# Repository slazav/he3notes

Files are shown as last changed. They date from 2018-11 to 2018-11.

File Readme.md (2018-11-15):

Work reports and notes.
- Folders for each project.
- A tex file with all information and pictures.
- Supplementary files and folders with links from tex.

The idea is to have a complete pdf page with hyperlinks
which can be sent to any external person.

Update script put all files into SITE folder and syncronizes
it with my aalto page (https://users.aalto.fi/~zavyalv1/texts/)

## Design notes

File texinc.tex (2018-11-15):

% standard packages
\usepackage{amssymb}
\usepackage{euscript}
\usepackage{eurosym}
\usepackage{graphicx}
\graphicspath{{img/}}
\usepackage{color}
\usepackage{epsfig}
\usepackage{fullpage}
\usepackage[colorlinks=true]{hyperref}
\usepackage{titling}

% title style
\pretitle{\noindent\LARGE}
\posttitle{\\[1ex]}
\preauthor{\large}
\postauthor{,}
\predate{\large(}
\postdate{)}
\date{last update: \today}

% large page size
\oddsidemargin -1cm
\topmargin -1cm
\textwidth 18cm
\textheight 27cm
\pagestyle{empty}

% PDF figure (floating)
\newcommand{\image}[3]{
\begin{figure}[#1]
\begin{center}
\caption{\small#3}

\label{image:#2}
\end{center}
\end{figure}
}

% simple image
\newcommand\simpleimage[3][\linewidth]{
\smallskip\begin{center}\vbox{\noindent
\\%
\parbox{#1}{\it#3}}\end{center}
\medskip}

%\newcommand\simpleimage[3][\linewidth]{
%\smallskip\vbox{\noindent
%\includegraphics[width=#1]{#2}\\%
%\it#3}
%\medskip}

% companies
\def\SchaefferAG{\href{https://www.schaeffer-ag.de/en/}{Schaeffer-AG}}
\def\MultiCB{\href{https://portal.multi-circuit-boards.eu}{Multi-CB}}
\def\BlueFors{\href{https://www.bluefors.com/}{BlueFors}}

\def\Ohmite{\href{https://www.ohmite.com}{Ohmite}}
\def\Firmetal{\href{http://www.firmetal.com}{Firmetal}}
\def\Bruker{\href{https://www.bruker.com}{Brucker}}

% use this to refer to Farnell and RS numbers:
\def\FarnellN#1{\href{https://fi.farnell.com/#1}{Farnell:#1}}
\def\RSN#1{\href{https://fi.rsdelivers.com/productlist/search?query=#1}{RS:#1}}

% products:
\def\OhmiteOFOD{\href{https://www.ohmite.com/assets/docs/res_od_of_oa.pdf}{Ohmite OF/OD series}}

% Supplementary materials on github <report> <file>
\def\GitFile#1#2{\href{https://github.com/slazav/he3notes/raw/master/#1/#2}{#1/#2}}

% Supplementary materials on my users.aalt.fi page
\def\WWWFile#1{\href{https://users.aalto.fi/~zavyalv1/#1}{#1}}

%progams
\def\MagnettiProg{\href{https://github.com/slazav/magneetti}{\tt magnetti}}

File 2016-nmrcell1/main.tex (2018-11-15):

\documentclass[a4paper]{article}
\input{../texinc.tex}

\title{NMR cell N1 (2016)}
\author{V.Zavjalov}

\twocolumn
\begin{document}
\maketitle

A simple cell for testing NMR in superfluid $^3$He. A Stycast-1266 cylindrical cell,
diameter 7.8~mm, height 10~mm, filling line 1~mm.

All drawings: \WWWFile{notes/2016-nmrcell1/draw.zip}\\
NMR magnet text: \WWWFile{notes/2016-nmrmag.pdf}

\simpleimage{img/cell_plan.png}{RF coil former (left) and the cell (right)}

\simpleimage{img/cell_parts.jpg}{Cell parts}

Copper cell leg was annealed at $900^\circ$C for 2h, brass spacer was
hard-soldered. Cleaning have been done in boiling water (to remove flux),
and then in boiling water with vinegar and baking soda to remove oxide. Note,
that brass became a copper-colored after soldering because Zn goes away.

Small quartz fork (32kHz) have been put into the cell leg about 1 cm from
its bottom. Cell leg have been glued into the cell with Stycast-1266.
Wires from the fork go through the glue.

Fork measurement at room temperature:\\
$P=1$~bar: $1/\tau=17.22$~1/s, $f=32743.76$~Hz\\
$P=0$~bar: $1/\tau=1.364$~1/s, $f=32750.69$~Hz

\simpleimage{img/cell_glue.jpg}{Cell leg (hard-soldered); fork (can is opened); gluing the cell}

Two pairs of RF coils are mounted on a separate plastic holder. Each pair has 34+34 turns
of 70mkm(?) Cu wire. Copper wires are in thermal contact with the mixing chamber.
Measured inductance, capacitance and resistance (with ~30cm wires):\\
coil 1: $L = 55.6\,\mu$H, $C = 14.2$~pF, $R = 14.4\,\Omega$\\
coil 2: $L = 55.4\,\mu$H,  $C = 15.7$~pF,  $R = 14.6\,\Omega$\\
Mutual capacitance about 10~pF.

Calculated magnetic field in the center: 16.6~G/A.
Calculation script (uses \MagnettiProg{} program) and field profile (text table):
\WWWFile{notes/2016-nmrcell1/rfcoil\_calc.zip}

\simpleimage{img/rfcoil_parts.jpg}{Parts of RF coil former}

\simpleimage{img/rfcoil.jpg}{RF coil (final version is on the right)}

\simpleimage{img/cell_finished.jpg}{Cell is mounted on the flange; centering RF coils}

\simpleimage{img/cell_magn.jpg}{The cell and the magnet}

RF coil forms a resonant circuit with a capacitor. A relay box (todo: text)
is used to switch the capacitance from 400 to 2400~pF.

Resonance curves measured at room temperature with a generator and a
lock-in, matlab script for fitting (not good):
\WWWFile{notes/2016-nmrmag/res300K.zip}. At frequency 800~kHz mutual inductance
and parasitic capacitance between coils compensates each other and
coupling goes to zero. This is an ideal situation for such
NMR coil design.

\simpleimage{img/resonance.png}{Resonances at room temperature}

Noise measured at room temperature:\\
\WWWFile{notes/2016-nmrmag/noise300K.zip}

\simpleimage{img/noise300K.png}{Coil noise at room temperature}

{\bf Drilling the cell (2018-01-18).} During glueing the cell filling line
was blocked. The filling line was drilled through the top wall of the cell,
then the hole was glued with a small GRP part.

\simpleimage[3cm]{img/drilling.jpg}{Drilling the cell}

{\bf RF-field calibration in the HPD experiment.} For $U_{\mbox{exc}}=1$~V
voltage on the coil is 0.05~V (HiZ mode of the generator + 20~dB
attenuator). Assuming the inductance~$L=55\,\mu$H and the
frequency~$f=1.120$~MHz one have the current~$I=0.13$~mA and field
$2.14$~mG/V in the center. Dimensionless field is $6.2\times10^{-6}$.

\end{document}

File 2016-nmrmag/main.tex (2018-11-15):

\documentclass[a4paper]{article}
\input{../texinc.tex}

\title{NMR magnet}
\author{V.Zavjalov}

\twocolumn
\begin{document}
\maketitle

NMR magnet for $^3$He experiments in DryDemag cryostat (summer 2016). The bottom flange
is connected to the nuclear demagnetization stage sinter volume. There is
a 6mm CuNi tube for soldering an experimental cell. The coil former is
thermally separated from the nuclear stage by Nb shield (Note: now the
lower part of the coil former is touching the shield. If one makes a
design with a gap there it will be much smaller heat leak through
niobium). The shield fully encapsulates the magnet. In the shield there
is a D6 hole for the cell leg, D3 and D4 screw holes near corners (where
marnetic field is small) and possible gap between Nb tube and top/bottom
plates.

\simpleimage[6cm]{img/solenoid_plan.png}{}
\simpleimage{img/solenoid.jpg}{Solenoid and testing frame}

The coil former and flanges have been made of oxigen-free copper in LTL
workshop and then annealed for 2 hours at 900$^\circ$C in
$2\cdot10^{-3}$~mbar of air (remove hidrogen, oxidize magnetic
impurities, anneal copper for better conductivity). Niobium parts have
been ordered in \Firmetal{} company (534\euro{} for the
$60\times1\times140$~mm tube, 153\euro{} for $65\times140\times1$~mm
plate).

All drawings: coil former, flanges, niobium shield, contact plate,
testing flange: \WWWFile{notes/2016-nmrmag/draw.zip}

\simpleimage{img/parts.jpg}{Magnet parts}

\simpleimage{img/parts_ann.jpg}{Copper parts after annealing}

\subsection*{Magnet calculation}
Coil calculations and optimisation have been done with \MagnettiProg{} program.\\
Optimization details:\\
\WWWFile{notes/2016-nmrmag\_calc.pdf}\\
Script for optimization:\\
\WWWFile{notes/2016-nmrmag/calc\_scr.zip}\\
Calculated field profiles (text table):\\
\WWWFile{notes/2016-nmrmag/calc\_res.zip}

\simpleimage{img/field_prof.png}{Calculated field profiles}

\subsection*{Magnet winding}

Winding was done 20-21.9.2016. Before winding a plastic rod with
longitudinal grooves on the surface have been inserted in the coil former
to prevent its deformation. After winding it was removed by drilling.

{\bf Wire.} Vacryflux 5001. 54 NbTi filaments in Cu matrix; diameter:
$70\mu$m without isolation, $83-85\mu$m with isolation; Cu/NbTi ratio:
1.35/1; critical current: 2~A at 3~T, 1~A at 8~T; resistance at room
temperature $8.0\Omega/$m; bought from \Bruker. Stycast-1266 was used to
fill the coil.

\simpleimage{img/winding.jpg}{Winding process}

{\bf Main coil:} length 104~mm, inner diameter 42~mm. Winding:
5 layers: 1208+1197+1200+1203+1193 turns. Accurate everywhere except
~4mm edges (hard to move from one layer to another with such a thin
wire). Then flatten edges with 12mm Kapton. Then 3 layers 11.2mm (compensation + 6thlayer):
140+97+120 turns. Then middle part of the 6th layer: 939 turns. Then
3 layers 11.2mm (compensation + 6thlayer): 133+103+133 turns.
Number of turns in the compensation coils is the same on both sides,
but it is a bit smaller then it should be.

{\bf Quadratic coil.} $L=34.8$, 2 layers, 408+408 turns.
After the coil had been made, the solenid was fully covered with Kopton
tape, and then by two layers of white paper to make a flat surface for
next coils.

{\bf Gradient coil.} Start at 2mm from solenoid edges, L=41.8mm R=~21.5
1 layer, 514+482 turns (not so accurate andassymetric).
Then the central part was covered with red "yellow" tape to make it flat
for the next coil.

{\bf Forth-power coil.} 1 layer, 79+79 turns, 6.8mm + 14mm gap + 6.0mm
(very assymetric for some reason).

\simpleimage{img/main_coil.jpg}{Main coil}

\simpleimage{img/grad_coil.jpg}{Gradient coil}

\simpleimage{img/coil.png}{Coil layout}

{\bf Connector:} plastic body + brass screws and nuts +
two-sided 0.4mm PCB (one side for contacts, another one for heat sink).
Wires are soldered to the connector at length 20-30cm (isolation was
removed in boiling NaOH).

\simpleimage{img/conn.jpg}{Connector}

\simpleimage{img/final.jpg}{Flanges}

\subsection*{Solenoid parameters}

Field profile, calculated and measured by shift of $^3$He NMR line:

\medskip
\begin{tabular}{llll}
Coil  &  Field [G/A] vs r,z [cm] & measured\\\hline
Main   &  $397.996$                       & $407.72$\\
Grad   &  $31.4270\ z$                    & $1.43 + ? z$\\
Quad   &  $105.958 - 15.240 f_2$$^{(1)}$  & $108.27 - ? f_2$\\
Helm   &  $16.6512 - 1.0351 f_4$$^{(2)}$  & $18.09 - ? f_4$\\
\end{tabular}

\noindent
(1) $f_2 = z^2-r^2/2$\\
(2) $f_4 = z^4 - 3 z^2 r^2 + 3/8 r^4$
\medskip

For comparison, Rota quadratic coil in magnon condensate experiments was $2.231 - 3.304 f_2$

Errors, calculated in cylindrical volumes with length = diameter 10 and 20 mm,
and measured by normal $^3$He NMR line width.

\medskip
\begin{tabular}{llll}
Coil   & Err 20x20 & Err 10x10 & Err (measured) \\\hline
Main   & $1.4\cdot10^{-5}$ & $2.2\cdot10^{-6}$ & $\approx1\cdot10^{-4}$\\
Grad   & $1.5\cdot10^{-2}$ & $3.5\cdot10^{-3}$ & \\
Quad   & $4.9\cdot10^{-3}$ & $3.0\cdot10^{-4}$ & \\
Helm   & $1.8\cdot10^{-1}$ & $2.2\cdot10^{-1}$ & \\
\end{tabular}
\medskip

Coil resistances:

\medskip
\begin{tabular}{ll}\hline
Main: & 7980~$\Omega$\\
Grad: & 1068~$\Omega$\\
Quad: & 861~$\Omega$\\
Helm: & 174~$\Omega$\\
\end{tabular}
\medskip

On the connector all coils are shortened by 100~$\Omega$ resistors to
provide LR filtering.

\subsection*{Problems and ideas}

1. Cut lower flange of the coil former to avoid contact with niobium shield and
decrease heat conductivity. I am not sure that this can be done accurately.
Also I'm not sure that this heat leak source is important.

2. Problem with the gradient coil: measurement gives approximately 1/2 of the
calculated value (15~G/cm/A). A stupid mistake somewhere...

3. One lead of the main coil is connected to the ground. Probably, can
not be fixed.

\end{document}

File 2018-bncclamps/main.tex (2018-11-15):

\documentclass[a4paper]{article}
\input{../texinc.tex}

\title{BNC clamps}
\author{V.Zavjalov}

\twocolumn
\begin{document}
\maketitle

In CW NMR experiments with compensated signal unstable contact in BNC
connectors is a problem. Unfortunately, most of usual devices use such
connectors for signal lines. There are a few ways how one can deal with
this problem. In Dmitriev's group in Moscow all important connectors have
been replaced to TNC (a threaded version of the BNC). This needs
disassembling of devices and not always possible. In ROTA group in
Helsinki clamps have been used to attach BNC-to-SMA converters to all
connectors.

\simpleimage{img/clamp_rota.jpg}{ROTA clamp}

I am using similar clamps as in ROTA but simpler and cheaper. Clamps have
been ordered in \SchaefferAG{} company. Price was 332\euro{} for 20
aluminum clamps (two parts each). Aluminum is a bit too soft, one should
try thicker design or different metal. But clamps work pretty well.

\noindent Clamp drawing, FPD files for production:\\
\WWWFile{notes/2018-bncclamps/fpd\_v1.zip}

\begin{center}
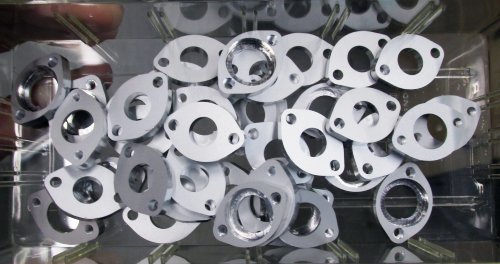
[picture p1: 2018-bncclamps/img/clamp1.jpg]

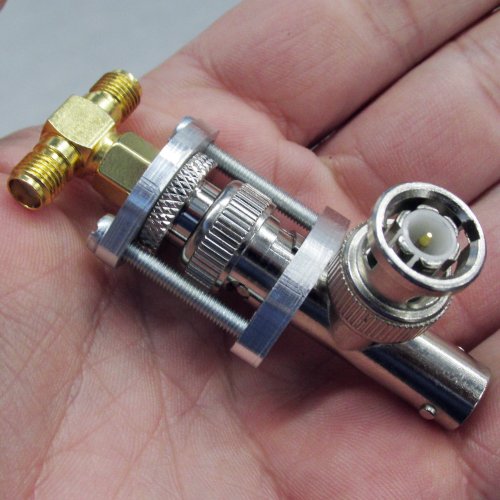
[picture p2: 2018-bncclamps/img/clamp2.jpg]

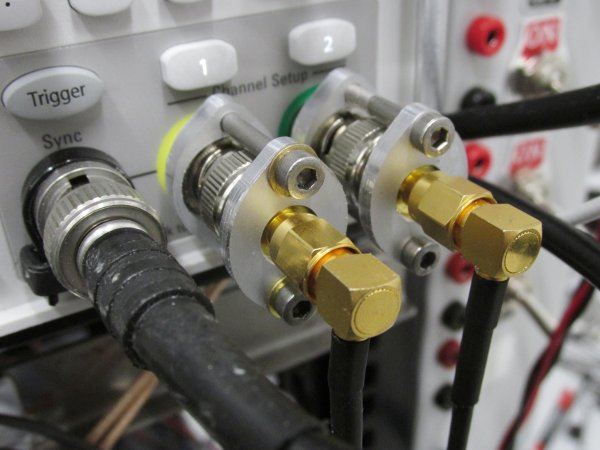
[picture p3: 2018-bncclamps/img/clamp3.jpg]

\end{center}

\end{document}

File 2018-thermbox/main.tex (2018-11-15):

\documentclass[a4paper]{article}
\input{../texinc.tex}

\title{Carbon thermometers for dilution fridges}
\author{V.Zavjalov}

\twocolumn
\begin{document}
\maketitle

The goal is to make standard thermometers for use in dilution fridges. I
use carbon \Ohmite{} resistors (\OhmiteOFOD{}, \FarnellN{2427380},
\FarnellN{2427405}, \RSN{892-5449} etc.), which are claimed to be
good thermometers at millikelvin temperatures~\cite{therm_paper}. The
series OD and OF have different sizes (diameter $2.5$~mm and~$3.8$~mm and
length~$7$~mm and~$10$~mm respectively). I grind resistors down to
approximately $0.7$~mm thickness and glue it in a slit in a copper box
using Stycast 2850. This provides a good thermal contact with the box,
mechanical stability, and protection against moisture.

\begin{center}
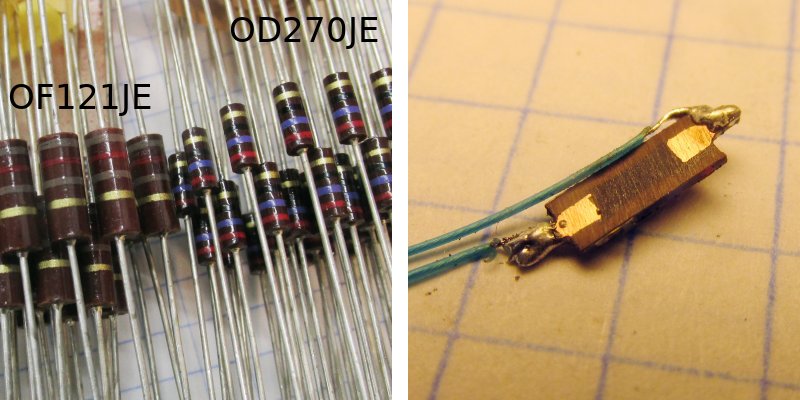
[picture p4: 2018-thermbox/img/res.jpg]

\end{center}

Copper boxes are ordered in \SchaefferAG.  The
box has $30\times30\times5$~mm size. It contains a~$20\times18\times3$~mm
compartment for RC lowpass filters, a $1\times16\times4$~mm slit for the
resistor and a~$16\times7\times3$~mm additional compartment which can be
used for sample chips. Holes are compatable with standard~$20\times20$ M4
hole grid on \BlueFors{} refrigerator plates. Drawings in FPD format are
available~\cite{box_drawings}, price was 315\euro{} for 10 boxes and 10
lids.

\begin{center}
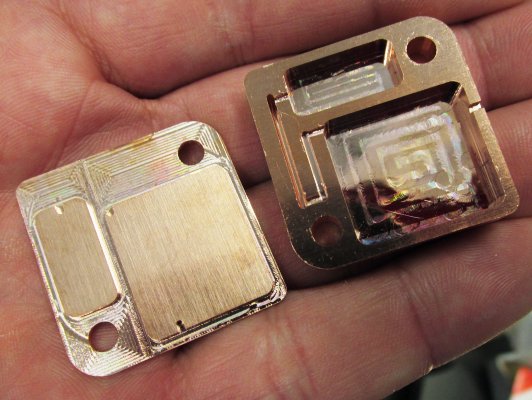
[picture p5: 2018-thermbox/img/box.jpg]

\end{center}

PCBs for filters are ordered in \MultiCB. Price
is 75\euro{} for 10 boards with two different filters and two small
sample plates each. Kicad project~\cite{filterpcb-kicad} and Gerber
files~\cite{filterpcb-gerber} are available.

To connect thermometers to BlueFors 4-pin sockets we use inserts
of LEMO {\tt FFA.0S.304.CLAC44} connectors (\FarnellN{2442870}).

\begin{center}
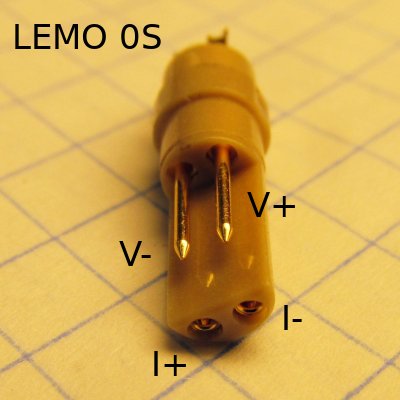
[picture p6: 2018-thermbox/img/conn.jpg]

\end{center}

\subsection*{List of devices}

\noindent
\begin{tabular}{|ll lll l|}\hline
N& Resistor& $R_0$ & $R_1$ & $R_2$ & \\
\hline
2018-11-02 N1&OD270JE& 27  & 56  & 56.0&\\
2018-11-02 N2&OD270JE& 27  & 59  & 64.4&\\
2018-11-02 N3&OF121JE& 120 & 231 & 277&\\
\hline
\end{tabular}
\medskip

Here $R_0$, $R_1$, and $R_2$ are nominal resistance, resistance after
grinding, and resistance after soldering and glueing. Change during
glueing probably means that contacts with carbon in the resistor
after grinding are not stable.

{\bf Work in progress...}

\begin{thebibliography}{}
\bibitem{therm_paper}
N. Samkharadze, A. Kumar, G. A. Cs{\'a}thy,
A New Type of Carbon Resistance Thermometer with.Excellent Thermal Contact at Millikelvin Temperatures,
{\it JLTP}, {\bf 160}, 246--253 (2010),\\
\url{https://doi.org/10.1007/s10909-010-0192-5}

\bibitem{box_drawings}
Box drawing in FrontPanel Disigner format, for production,\\
\WWWFile{notes/2018-thermbox/box\_v1.zip}

\bibitem{filterpcb-kicad}
Filter PCB, KiCAD project,\\
\WWWFile{notes/2018-thermbox/pcb\_kicad.zip}

\bibitem{filterpcb-gerber}
Filter PCB, Gerber files for production,\\
\WWWFile{notes/2018-thermbox/pcb\_v1.zip}

\end{thebibliography}
\end{document}

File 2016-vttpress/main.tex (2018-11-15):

\documentclass[a4paper]{article}

\input{../texinc.tex}

\title{Calibration of VTT pressure sensor}
\author{V.Zavjalov}

\twocolumn
\begin{document}
\maketitle

{\bf Experimantal setup.} For measurements we used Andeen-Hagerling AH
2500A capacitance bridge working at 1~kHz. The voltage~$U$ applied by the
bridge to the pressure sensor can be chosen in the range from 0.5~mV to
15~V RMS. At~$U>1$~V the noise of the measurement was about
$1\cdot10^{-3}$~pF, this corresponds to the pressure variations of about
$0.3$~mbar. Pressure was measured by Wallace \& Tiernan absolute pressure
gauge with working range $0\ldots1$~bar and resolution $\sim 0.3$~mbar.
%(For low pressure measurements we also use Agilent FRG-730 Pirani gauge.)
Temperature was measured by PT1000 platinum thermometer.

%%%%%%%%%%%%%%%%%%%%%%%%%%%%%%%%%%%%%%%%%%%%%%%%%%%%%%%%%%
\image{h}{pcal}{Fig.~1. (A) Capacitance of the pressure sensor as a
function of pressure. Measurements for three exctation voltages (red 15
V, green 7.5 V, blue 1.5 V) and two temperatures (circles 295~K, squares
77.2~K) are shown. Lines are fits to the model~(\ref{eq:mod}), made
separately for each temperature. Data for other voltage values (3~V,
0.75~V, 0.35~V, 0.25~V, 0.1~V) was used for fitting, but not shown on the
picture.
(B) Difference between measured data and
model~(\ref{eq:mod}). Same data as on (A) are presented. }
%%%%%%%%%%%%%%%%%%%%%%%%%%%%%%%%%%%%%%%%%%%%%%%%%%%%%%%%%%

{\bf Pressure dependence.} We found that at constant temperature the
capacitance~$C$ of the pressure sensor as a function of pressure~$P$ and
applied voltage~$U$ can be fit by a model with four parameters, $C_0$,
$C_1$, $P_0$, $U_0$:
\begin{equation}\label{eq:mod}
C = C_0 + C_1\ \frac{1}{d},
\end{equation}
where $d$ is determined by a non-linear equation:
\begin{equation}
d = 1 - \frac{P}{P_0} - \left(\frac{1}{d}\ \frac{U}{U_0}\right)^2.
\end{equation}
In this model the sensor is treated as a sum of a constant capacitor
$C_0$ and a flat capacitor $C_1$ with dimensionless distance~$d$ affected
linearly by applied force. One component of the force is proportional to
the pressure and another one is electrostatic force proportional to $U^2/d^2$. In
this model the capacitor is collapsed at $P=P_0$ or
$U=2/(3\sqrt{3})\,U_0\approx 0.385\,U_0$. We checked that above~$\approx 1.6$~bar
loss in the capacitor grows quickly and it becomes imposiible to measure
the capacitance.

Fig. 1 shows measured capacitance as a function of~$P$ and~$U$ at room
temperature (295 K) and temperature of liquid nitrogen (77.2~K). One can
see that model works well everywhere except the region of high pressures
and high excitation voltages (this corresponds to the smallest values of
distance~$d$). At small exitation voltages ($<3V$) the model gives us the
accuracy $\sim 10^{-3}$~pF comparable to the noise in the capacitance measurement.

Measured parameters for room temperature (295K), temperature of liquid
nitrogen (77.2 K) and temperature of liquid helium (4.2K) are in the
table:

\begin{tabular}{lll}
$T$, K & $C_0$, pF          & $C_1$, pF \\\hline
295.04 & $24.0821\pm0.0084$ & $9.0052\pm0.0082$\\
77.2   & $23.4230\pm0.0065$ & $8.8738\pm0.0064$\\
4.2    & $23.3702\pm0.0098$ & $8.8544\pm0.0096$\\
\hline
\end{tabular}

\begin{tabular}{llll}
$T$, K & $P_0$, bar & $U_0$, V RMS\\\hline
295.0 & $2.9864\pm0.0019$ & $178.854\pm0.691$\\
77.2  & $3.0082\pm0.0015$ & $179.846\pm0.530$\\
4.2   & $3.0043\pm0.0023$ & $171.643\pm0.713$\\
\hline
\end{tabular}
\medskip

%{\bf Temperature dependence.}
%Measurements similar to Fig.~1 are done at several temperatures giving us
%parameters $C_0$, $C_1$, $\alpha$ and~$\beta$. We also performed
%measurements of the capacitance during slow heating at 0 and 1 bar with
%various voltages~$U$.
%
%TODO

{\bf Helium diffusion.} In helium atmosphere pressure readings of the
sensor start to shift because of diffusion of helium inside the sensor
inner volume. In air or vacuum the diffusion goes in the opposite
direction, restoring the original readings. This effect exist only at
high temperatures. At room temperature we observed filling of the inner
volume with time constant $\sim2.5$~h. At temperature of liquid nitrogen
(77.2~K) we have not observed any visible change during 15~h
(See Fig~2.).

%%%%%%%%%%%%%%%%%%%%%%%%%%%%%%%%%%%%%%%%%%%%%%%%%%%%%%%%%%
\image{h}{hdiff}{Fig.~1. Helium diffusion. At room temperature
(295 K) helium diffuse into sensor's inner volume, filling it with time
constant $\sim 2.5$~h. At temperature of liquid nitrogen no diffusion have
been observed.}
%%%%%%%%%%%%%%%%%%%%%%%%%%%%%%%%%%%%%%%%%%%%%%%%%%%%%%%%%%

\end{document}

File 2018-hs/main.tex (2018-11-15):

\documentclass[a4paper]{article}
\input{../texinc.tex}

\title{Rebuilding heat switch and nuclear stage plate for DryDemag}
\author{V.Zavjalov}

%\twocolumn
\begin{document}
\maketitle

The goal is to make a detachable frame with the nuclear demagnetization
stage (NS) and the heat switch (HS). We try to get more rigid
construction, more space for experiment cells, better heat switch.

\subsection*{Old construction}

In the previous setup NS is mounted on a brass plate (which can be bad
because of large heat capacitance and small heat conductivity of brass).
The plate is hanging on four ceramic legs under the mixing chamber of
DryDemag refregirator~\cite{drydemag}.

\image{h}{old_setup}{}
%\begin{center}
%\includegraphics[width=\linewidth]
%\end{center}

Drawings:
\begin{itemize}
\item Assembly drawing (as on the figure above):\\
\GitFile{20181105-hs}{old\_nsframe\_assembly.pdf}

\item Old brass NS flange drawing:\\
\GitFile{20181105-hs}{old\_flange\_brass.pdf}

\item Old stage flange drawing:\\
\GitFile{20181105-hs}{old\_flange\_brass.pdf}

\end{itemize}

\subsection*{Old HS performance measurements}

\subsection*{HS papers}

\subsection*{Parts}

\begin{thebibliography}{}

\bibitem{drydemag}
I. Todoshchenko, J.-P. Kaikkonen, R. Blaauwgeers, P. J. Hakonen, A. Savin,
Dry demagnetization cryostat for sub-millikelvin helium experiments: Refrigeration and thermometry,
{\it Rev.Sci.Instr}, {\bf 85}, 085106 (2014),\\
\url{https://doi.org/10.1063/1.4891619}

\bibitem{nsframe_fpd}
NS frame (top, middle, and NS plates), FPD files used for ordering parts in Schaefer-AG
\url{nsframe_fpd.zip}

\end{thebibliography}
\end{document}

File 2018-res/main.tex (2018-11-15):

\documentclass[a4paper]{article}
\input{../texinc.tex}

\title{A resonator driven by external force}
\author{V.Zavjalov}

\begin{document}
\maketitle

\begin{tabular}{ll}
\hline\\[-2mm]

Equation: &
$\displaystyle
\ddot x = -\omega^2_0 x + \dot x /\tau + F\exp(i\omega t)$
\\[5mm]

Fourier component~$\omega$: &
$\displaystyle
-\omega^2 x = -\omega^2_0 x + i \omega x /\tau + F$
\\[5mm]

Complex amplitude: &
$\displaystyle
x(\omega) = \frac{F}{\omega_0^2 - \omega^2 - i \omega /\tau}$

\\[5mm]\hline\\[-2mm]

Dispersion: &
$\displaystyle
\Re(x) = F\ \frac{\omega_0^2 - \omega^2}
                {(\omega_0^2 - \omega^2)^2 + (\omega /\tau)^2}$
\\[5mm]
Dispersion max/min: &
$\displaystyle
\omega_m^2 = \omega_0^2 \left(1 \pm \frac1{\omega_0\tau}\right),
\qquad \Re(x) = \mp \frac{F\tau} {2\omega_0 \pm 1/\tau}$
\\[5mm]
Dispersion zero: &
$\displaystyle
\omega_z = \omega_0$

\\[5mm]\hline\\[-2mm]

Absorption: &
$\displaystyle
\Im(x) = F\ \frac{\omega /\tau}
                {(\omega_0^2 - \omega^2)^2 + (\omega /\tau)^2}$
\\[5mm]
Absorption maximum: &
$\displaystyle
\omega_m^2 = \frac13 (\omega_0^2-1/2\tau^2) + \frac13 \sqrt{(\omega_0^2-1/2\tau^2)^2 + 3\omega_0^4}$
\\[5mm]

at $(\omega_0\tau)^2 \gg 1$: &
$\displaystyle
\omega_m^2 \approx \omega_0^2 \left(1 - \frac1{(2\omega_0\tau)^2}\right),
\qquad
\Im(x) \approx \frac{F \tau}{\omega_0}
\left(1 + \frac1{(4\omega_0\tau)^2}\right)
$
\\[5mm]

$1/2$-height points:&
$\displaystyle
\omega_h \approx \omega_m \pm 1/2\tau
$

\\[5mm]

width at $1/\sqrt2$ height:&
$\displaystyle
d\omega \approx \frac1{\tau}
$

\\[5mm]\hline\\[-2mm]

Absolute value: &
$\displaystyle
|x| = \frac{F} {\sqrt{(\omega_0^2 - \omega^2)^2 + (\omega /\tau)^2}}
$\\[5mm]

Absolute value maximum: &
$\displaystyle
\omega_m^2 = \omega_0^2 \left(1 - \frac1{2(\omega_0\tau)^2}\right),
\qquad
|x| = \frac{F\tau}{\omega_0} \left(1 - \frac1{(2\tau\omega_0)^2}\right)^{-1/2}
$
\\[5mm]

$1/\sqrt2$-height points:&
$\displaystyle
\omega_h^2 = \omega_0^2 - 1/2\tau^2 \pm \sqrt{ \omega_0^2/\tau^2 - 1/4\tau^4}
$
\\[5mm]

width at $1/\sqrt2$ height:&
$\displaystyle
d\omega \approx \frac1{\tau} \left(1 - \frac1{8(\tau\omega_0)^2}\right)
$
\\[5mm]\hline\\[-2mm]

\end{tabular}

\section*{Free decay}
\begin{tabular}{ll}
\hline\\[-2mm]

Equation: &
$\displaystyle
\ddot x = -\omega^2_0 x + \dot x /\tau$
\\[5mm]

Solution: &
$\displaystyle
x = C \exp(wt),
\qquad
w = \pm i \sqrt{ \omega^2_0 - 1/4\tau^2} + 1/2\tau
$
\\[5mm]

\end{tabular}

\image{h}{res}{}

\end{document}

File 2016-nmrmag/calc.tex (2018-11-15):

\documentclass[a4paper]{article}

\input{../texinc.tex}

\title{NMR magnet optimization}
\author{V.Zavjalov}

\begin{document}

\maketitle

The field is calculated in radial coordinates,~$r$ and~$z$.
We need to optimize at least three coil systems in the volume $V_0$: $r<r_0, |z|<z_0$:
\begin{itemize}
\item Homogeneous field produced by main solenoid and compensation coils
\item Gradient field
\item Minimum (quadratic) field
\end{itemize}
For this we calculate mean square difference from the best
constant, linear, or quadratic approximation.

$$ R = \sqrt{\frac{1}{V_0}\int_V(H(r,z) - H_0 - A f(z,r))^2\,dV}
$$

Function $f(z,r)$ can be chosen according with the fitting model:
$f(z,r)=0$ for constant field, $f(z,r)=z$ for gradient field, 
$f(z,r)=z^2-r^2/2$ for quadratic field or even $f(z,r) = z^4 - 3z^2r^2 + 3/8r^2$
for forth-order field.

The $-1/2$ ratio of~$r$ and~$z$ quadratic terms comes from Maxwell equations
for a cylindrically symmetric system (see below).

This can be rewritten as
$$ R^2
 = I_2 - 2H_0 I_1 + H_0^2 + A( A I_{f2} - 2I_{fH} + 2H_0 I_{f1})
$$

where we introduced integrals
$$
I_1 = \frac{1}{V_0}\int_V H(z,r)\, dV,\qquad
I_2 = \frac{1}{V_0}\int_V H(z,r)^2\, dV,\qquad
$$
$$
I_{fH} = \frac{1}{V_0}\int_V f(z,r) H(z,r)\, dV,\qquad
I_{f1} = \frac{1}{V_0}\int_V f(z,r)  \, dV,\qquad
I_{f2} = \frac{1}{V_0}\int_V f(z,r)^2\, dV,\qquad
$$

Parameters $H_0$ and $A$ correspond the minimum of~$R$:
$$
\frac{\partial R}{\partial H_0} = 0,\quad
\frac{\partial R}{\partial A} = 0
$$

$$
H_0 = I_1 - A I_{f1},\qquad
$$
$$
A = (I_{fH} - I_{f1} I_1)/(I_{f2} - I_{f1}^2),\qquad
$$

For coil optimizations we use dimensionless current-independent
parameters:
$R/|H_0|$ for constant field, $R/(z_0|A|)$ for gradient field, and
$R/(z_0^2|A|)$ for quadratic fields.

Optimization is done in $z0=r0=10$ cylindrical volume.

{\bf Main coil geometry.} We use main coil with length 104~mm, inner radius
21~mm, and 6 layers of wire in the cylindrical shield with length 140~mm
and radius 29~mm. Wire diameter is 0.084mm (in insulation).

{\bf Compensation coils.} Minimum value in the optimization is not so
important as the minimum width ($0.2$~mm error will break all the
improvements). It's better to start compensation coils from edge of the
main solenoid and make them thin (I use 2 layers) and long -- then the
minimum is wider. Shorter coils have better field homogeneity, but it is
harder to make accurate size. Second layer with different length does not
help much. Compensation coils inside the solenoid is slightly better, but
i decided to put them outside to adjust size after making and
recalculating the main solenoid. Also it is easier to wind the main solenoid
on a flat surface. The quadratic coil can improve the field
homogeneity even more.

{\bf Gradient coils} are better if they are wider. It is good to start
them from the edge of the solenoid. Starting from the end of compensation
coils is also fine (\%10 worse). Second layer with different length can
improve gradient accuracy $\approx 2$ times,

{\bf Quadratic coil} just a coil in the center with a certain width.

{\bf Optimization results:}\\
\medskip
\begin{tabular}{lllllll}
Coils & Edge &Length       & Layers & Err 20x20$^{(1)}$  & Err 10x10$^{(2)}$        & Field [G/A] vs r,z [cm] \\\hline
Main  & 52   & 104         & 6      & $6.6\cdot10^{-4}$ & $1.7\cdot10^{-4}$ & $397.086$\\
Comp  & 52   & 11.2        & 2      & $1.4\cdot10^{-5}$ & $2.2\cdot10^{-6}$ & $397.996$\\
Grad  & 50   & 41.8        & 1      & $1.5\cdot10^{-2}$ & $3.5\cdot10^{-3}$ & $31.4270\ z$\\
Quad  & -    & 34.8        & 2      & $4.9\cdot10^{-3}$ & $3.0\cdot10^{-4}$ & $105.958 - 15.240 (z^2-r^2/2)$\\
4-th  & 13.4 & 6.4         & 2      & $1.8\cdot10^{-1}$ & $2.2\cdot10^{-1}$ & $16.6512 - 1.0351 f_4$$^{(3)}$\\
\end{tabular}
\medskip

\noindent
(1) in the volume with length = diameter = 20 mm.\\
(2) in the volume with length = diameter = 10 mm.\\
(3) $f_4 = z^4 - 3 z^2 r^2 + 3/8 r^4$

\section*{Field distribution in a cylindrical simmetry (why $z^2+r^2/2$)}

Maxwell equations:
$$
\mbox{div} B = 0,\qquad
\mbox{rot} B = 0
$$

In symmetrical case ($\partial B/\partial\phi = 0, B_\phi=0$):
$$
\frac{\partial B_r}{\partial z} = \frac{\partial B_z}{\partial r}, \qquad
\frac{1}{r} \frac{\partial r B_r}{\partial r} + \frac{\partial B_z}{\partial z}=0.
$$

Multiply the first equation by $r$, differentiate by $r$, and then multiply by $1/r$.
Differentiane the second equation by $z$. Then one can exclude $B_r$:
$$
\frac{1}{r} \frac{\partial B_z}{\partial r}
 + \frac{\partial^2 B_z}{\partial r^2}
 + \frac{\partial^2 B_z}{\partial z^2}=0.
$$

For quadratic distribution $B_z = az^2 + br^2$ one have $a=-2b$.

For 4-power distribution $B_z \propto z^4 - 3 z^2 r^2 + 3/8 r^4$.

\section*{Critical current}

For calculated solenoid (main + compensation coils), maximum absolute
field on the coil is 0.110~T/A, on the shield is 0.843~T/A.
According with Bruker wire specification critical field is $(13-5I)$~T.
Critical field for Nb shield as about 0.15~T.

Thus the current limit introduced by shield is 1.35~A,
current limit by wire is 2.57~A. This corresponds to the
field in the middle 0.09~T and 1.71~T (???).

\end{document}

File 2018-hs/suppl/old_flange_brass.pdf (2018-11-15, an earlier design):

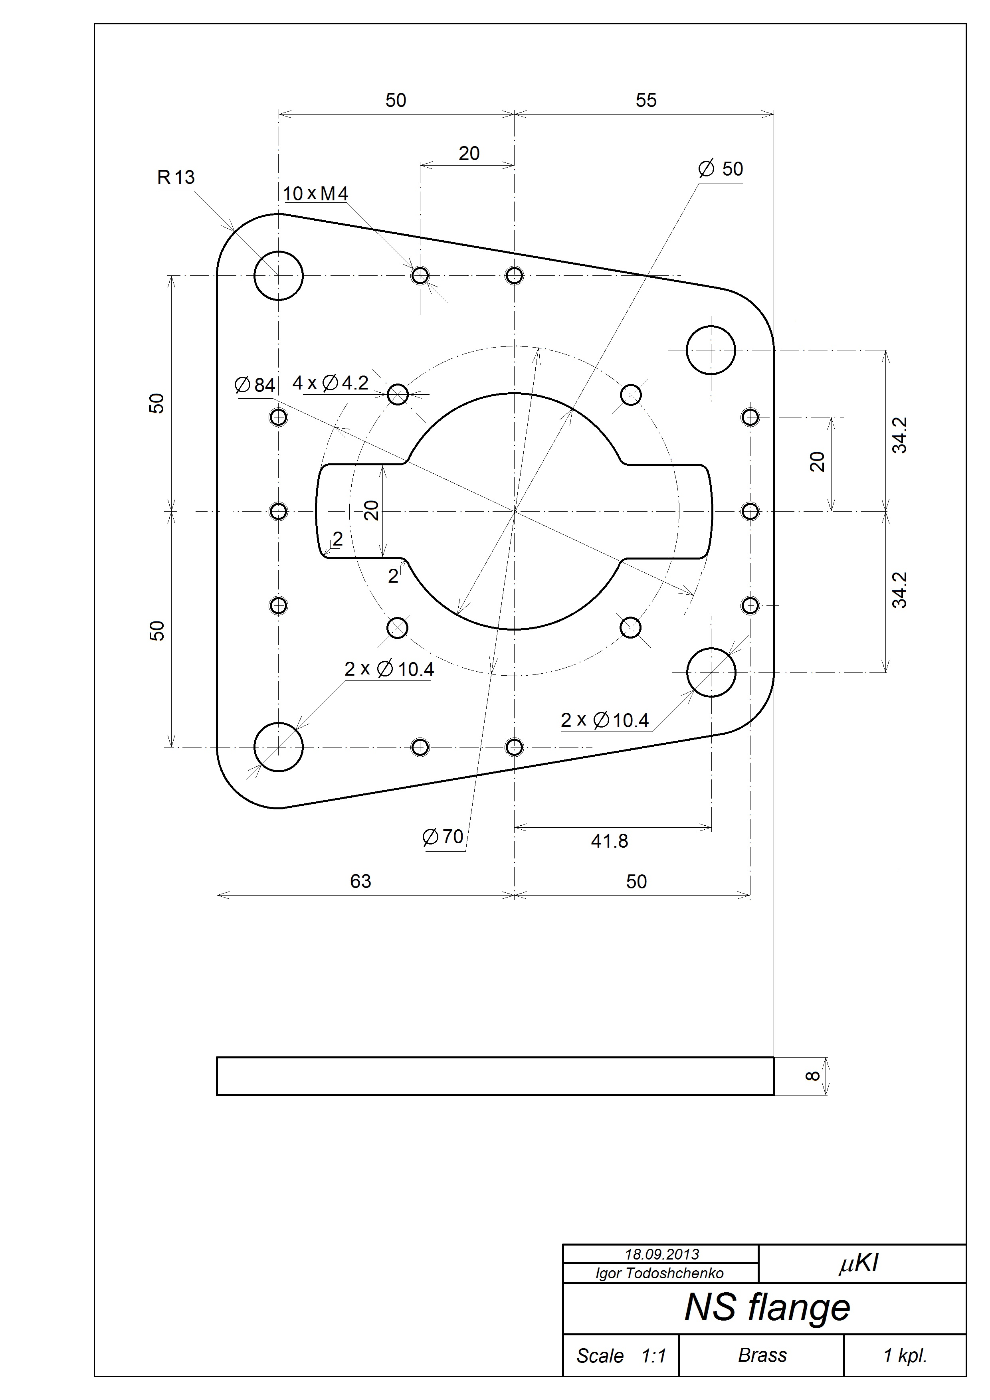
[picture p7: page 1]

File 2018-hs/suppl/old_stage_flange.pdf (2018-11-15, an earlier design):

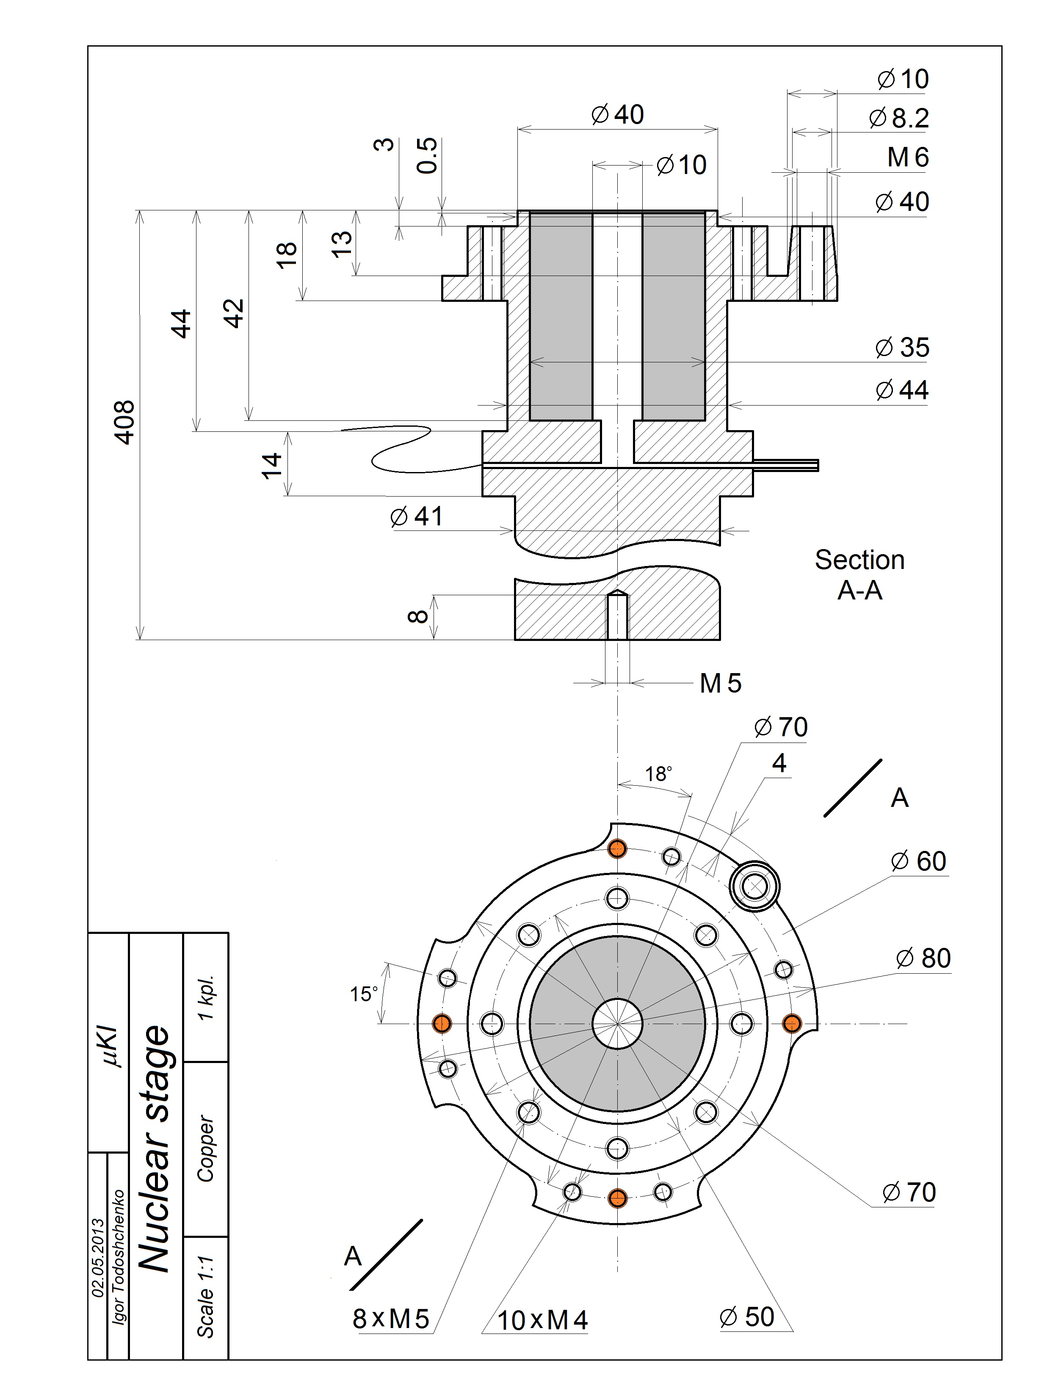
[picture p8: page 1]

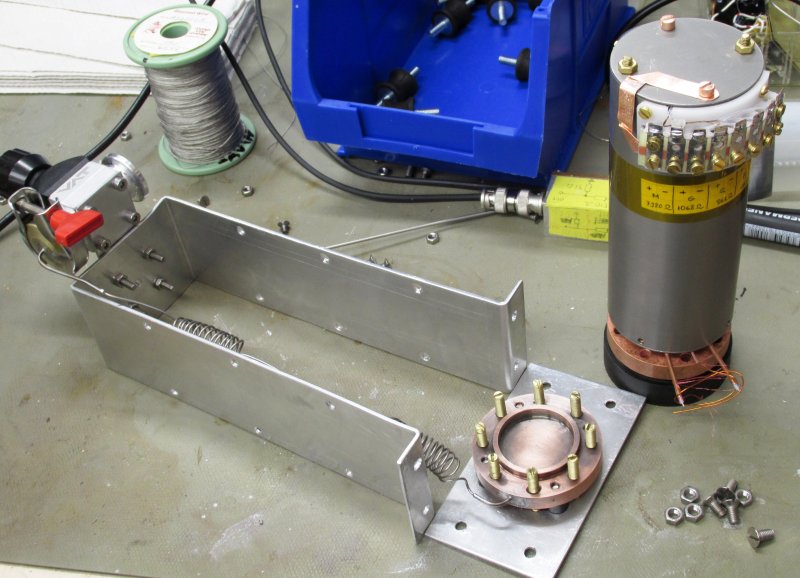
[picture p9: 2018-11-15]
2016-nmrmag/img/solenoid.jpg

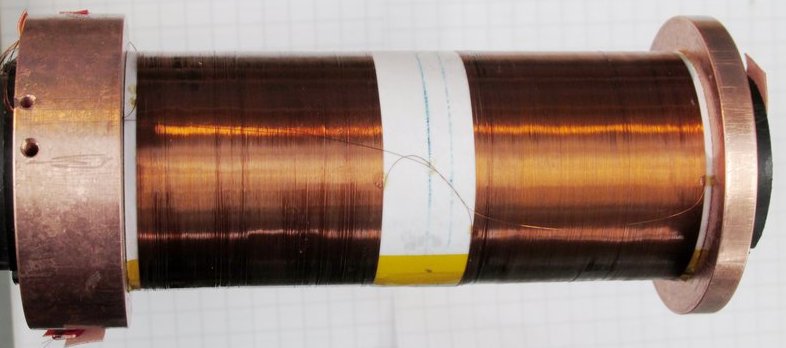
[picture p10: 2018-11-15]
2016-nmrmag/img/grad_coil.jpg

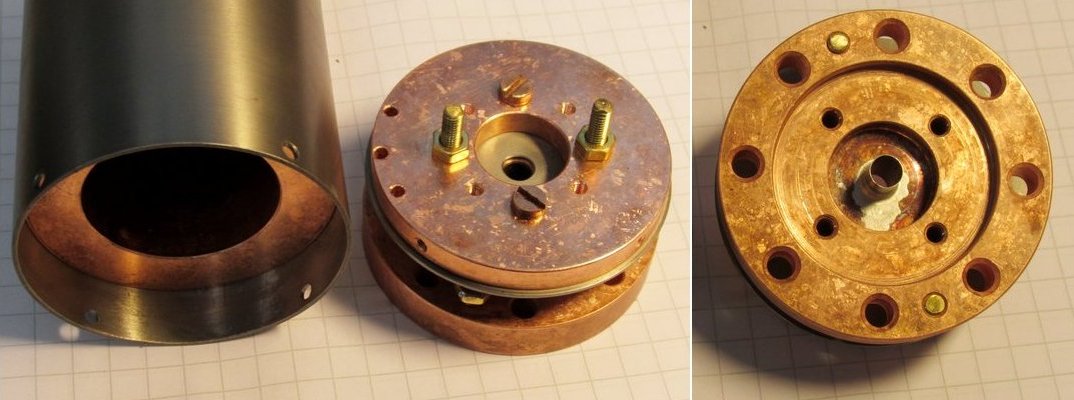
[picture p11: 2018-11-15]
2016-nmrmag/img/final.jpg

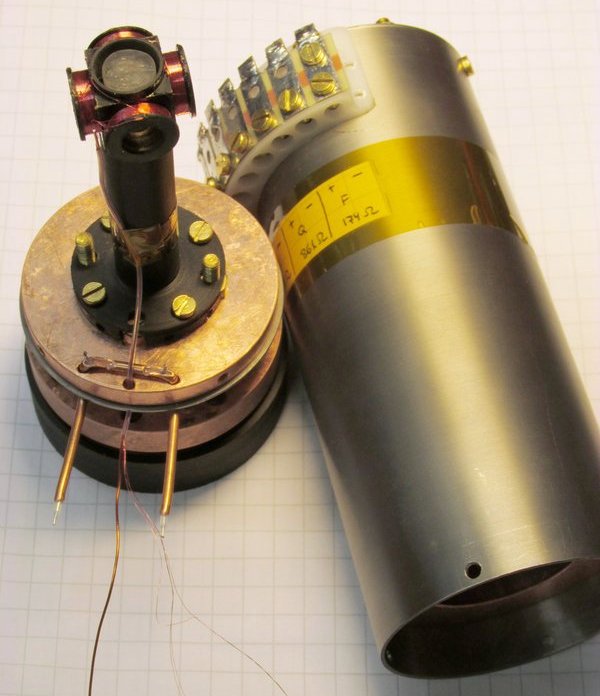
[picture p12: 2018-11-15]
2016-nmrcell1/img/cell_magn.jpg

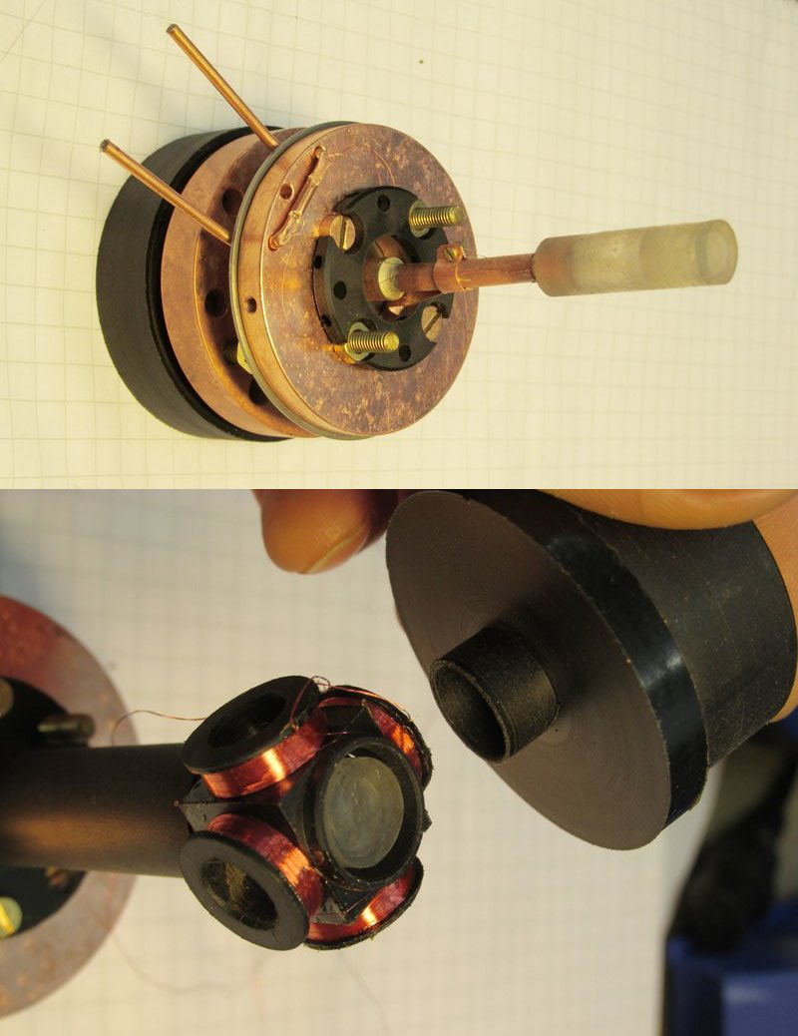
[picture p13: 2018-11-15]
2016-nmrcell1/img/cell_finished.jpg

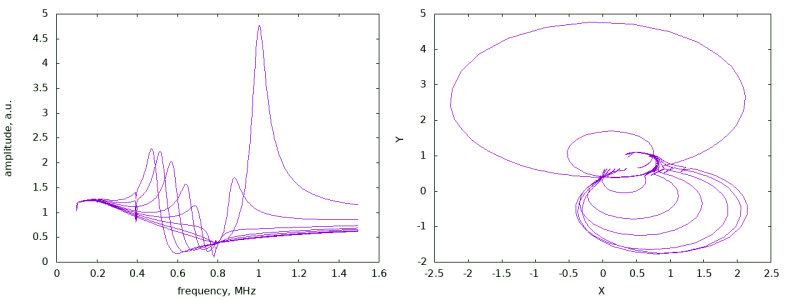
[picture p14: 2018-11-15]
2016-nmrcell1/img/resonance.png

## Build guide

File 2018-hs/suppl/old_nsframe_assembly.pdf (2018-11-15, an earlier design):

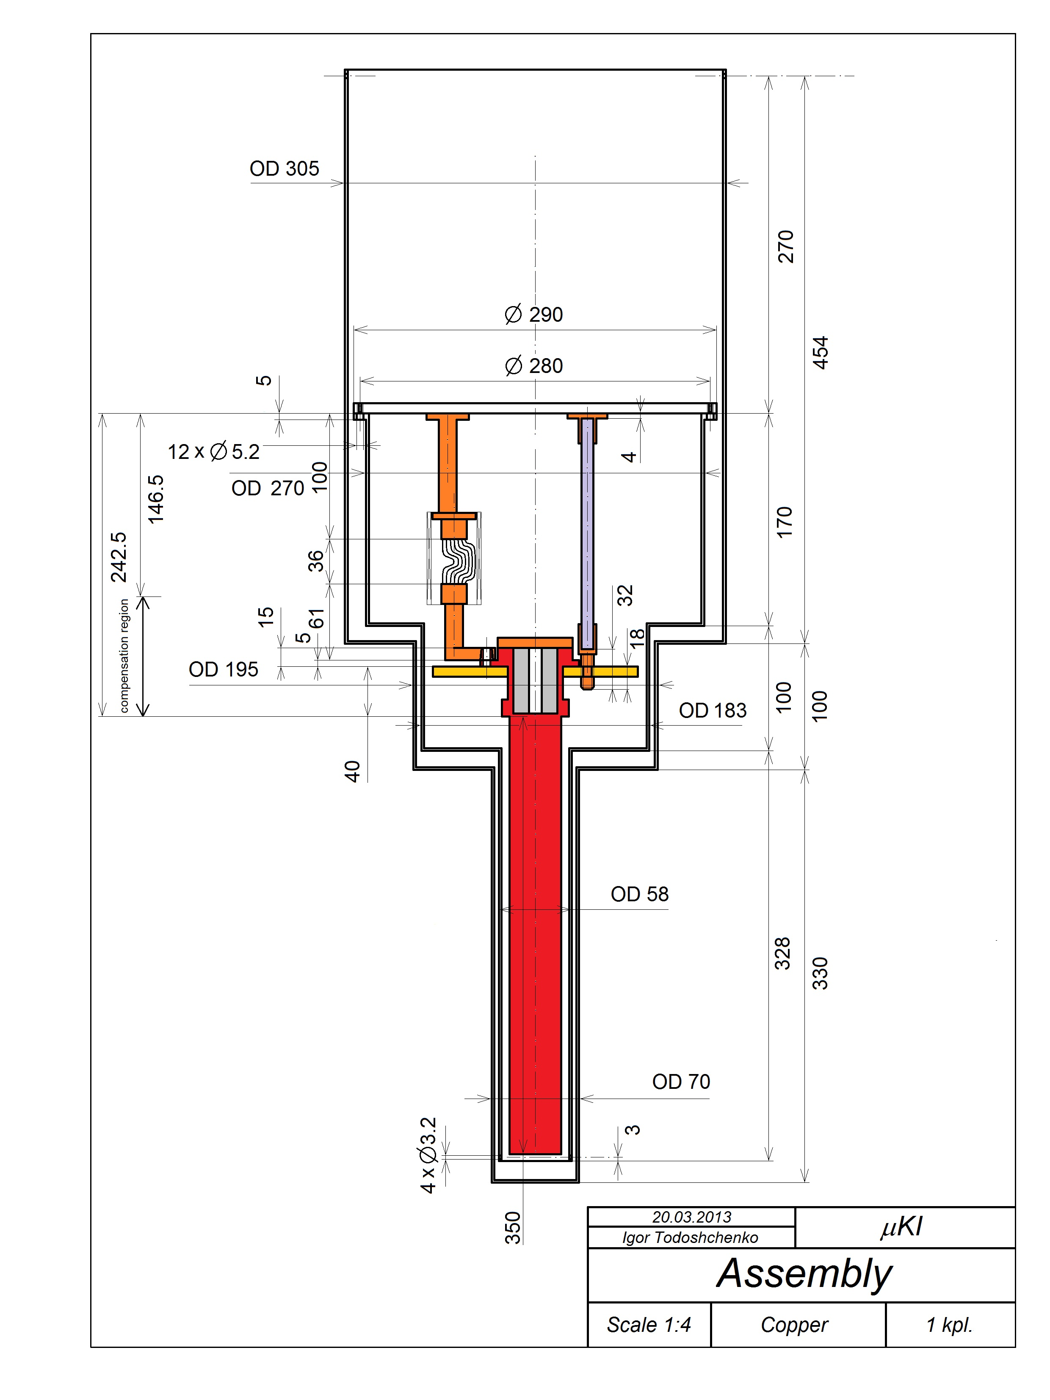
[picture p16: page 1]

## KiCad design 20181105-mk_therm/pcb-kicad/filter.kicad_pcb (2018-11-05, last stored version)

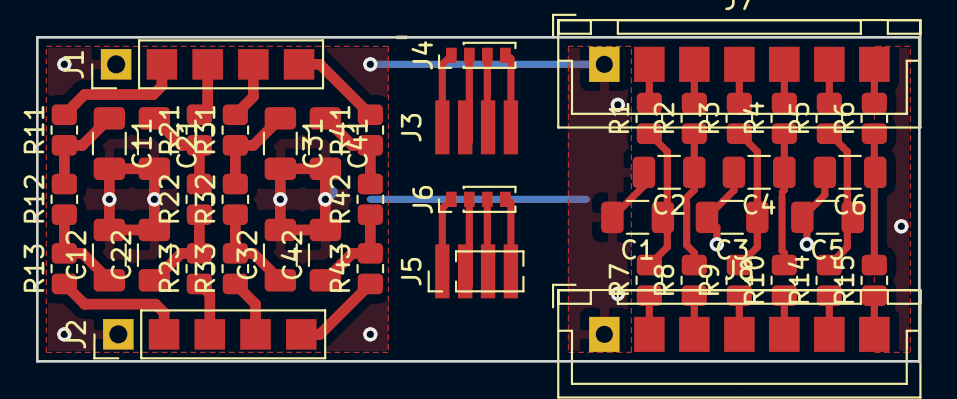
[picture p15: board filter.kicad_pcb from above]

Board: 2 copper layers, 49.0 x 18.0 mm, 46 parts (0 on the bottom side), 43 nets.

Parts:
C1, C2, C3, C4, C5, C6, C11, C12, C21, C22, C31, C32, C41, C42: C; C_1206_3216Metric
J1, J2: Conn_01x05_Male; PinHeader_1x05_P2.54mm_Vertical
J3, J5: Conn_01x04_Male; PinHeader_1x04_P1.27mm_Vertical
J4, J6: Conn_01x04_Male; PinHeader_1x04_P1.00mm_Vertical
J7, J8: Conn_01x07_Male; JST_XH_B07B-XH-A_1x07_P2.50mm_Vertical
R1, R2, R3, R4, R5, R6, R7, R8, R9, R10, R11, R12, R13, R14, R15, R21, R22, R23, R31, R32, R33, R41, R42, R43: R; R_0805_2012Metric

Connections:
GND: C1.2, C2.2, C3.2, C4.2, C5.2, C6.2, C11.2, C12.2, C21.2, C22.2, C31.2, C32.2, C41.2, C42.2, J1.1, J2.1, J7.1, J8.1
unnamed: C1.1, R1.1, R7.2
unnamed: C2.1, R2.1, R8.2
unnamed: C3.1, R3.1, R9.2
unnamed: C4.1, R4.1, R10.2
unnamed: C5.1, R5.1, R14.2
unnamed: C6.1, R6.1, R15.2
unnamed: C11.1, R11.1, R12.2
unnamed: C12.1, R12.1, R13.2
unnamed: C21.1, R21.1, R22.2
unnamed: C22.1, R22.1, R23.2
unnamed: C31.1, R31.1, R32.2
unnamed: C32.1, R32.1, R33.2
unnamed: C41.1, R41.1, R42.2
unnamed: C42.1, R42.1, R43.2
unnamed: J1.2, R11.2
unnamed: J1.3, R21.2
unnamed: J1.4, R31.2
unnamed: J1.5, R41.2
unnamed: J2.2, R13.1
unnamed: J2.3, R23.1
unnamed: J2.4, R33.1
unnamed: J2.5, R43.1
unnamed: J3.1, J4.1
unnamed: J3.2, J4.2
unnamed: J3.3, J4.3
unnamed: J3.4, J4.4
unnamed: J5.1, J6.1
unnamed: J5.2, J6.2
unnamed: J5.3, J6.3
unnamed: J5.4, J6.4
unnamed: J7.2, R1.2
unnamed: J7.3, R2.2
unnamed: J7.4, R3.2
unnamed: J7.5, R4.2
unnamed: J7.6, R5.2
unnamed: J7.7, R6.2
unnamed: J8.2, R7.1
unnamed: J8.3, R8.1
unnamed: J8.4, R9.1
unnamed: J8.5, R10.1
unnamed: J8.6, R14.1
unnamed: J8.7, R15.1
